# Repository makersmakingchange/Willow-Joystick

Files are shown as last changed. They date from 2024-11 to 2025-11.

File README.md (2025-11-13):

# Willow Joystick

## Overview
The Willow Joystick is a cost-effective, low force joystick that can be used for adaptive gaming or computer access. This joystick is intended for users with very low strength or range of motion. The joystick only requires about 25 grams of force to operate, and has a range of motion of ± 7.5° or about ±5 mm. 

The Willow Joystick has a variety of options for customizing it for the user:
 - Swappable Toppers: there are 7 different topper designs, including one that can be used with heat moldable polymer for a custom fit. 
 - Wrist Ramps: there are several wrist rest options for  supporting the user's arm.
 
The Willow is made up of the Willow Joystick and the Willow Hub. The Joystick is the primary user interface and contains a low-force Hall-Effect joystick. The Hub has a display that provides a graphical interface for independently adjusting settings, as well as it provides the connection to the host device and up to three external assistive switches with 3.5 mm jacks.

The Willow is compatible with a range of host devices that can support a USB Mouse, a USB Gamepad and/or a Bluetooth Mouse. Compatible devices include PC and Mac computers and laptops, Android, iOS, and Windows smartphone and tablets, and the Xbox Adaptive Controller. As a USB joystick, the Willow is not compatible with the Sony Playstation Access Controller.  

The joystick has adaptors for both ¼-20 mounting arms and RAM-B ball mount arms and has an optional nonslip base for use on a table. There is also a modifiable wrist ramp to help raise a user’s wrist while using the joystick.

The device is comprised of off-the-shelf electronics and hardware, a custom PCB and 3D printed parts. The overall cost of materials (including materials required in bulk) for a single build is about $180 (plus shipping). In larger quantities, the cost of materials is closer to $135.

The Willow Joystick is Open Assistive Technology (OpenAT) and is certified as Open Source Hardware by the Open Source Hardware Association under the OSHWA UID [CA000062](https://certification.oshwa.org/ca000062.html). Under the terms of the open source licenses, the device may be built, used, and improved upon by anyone.

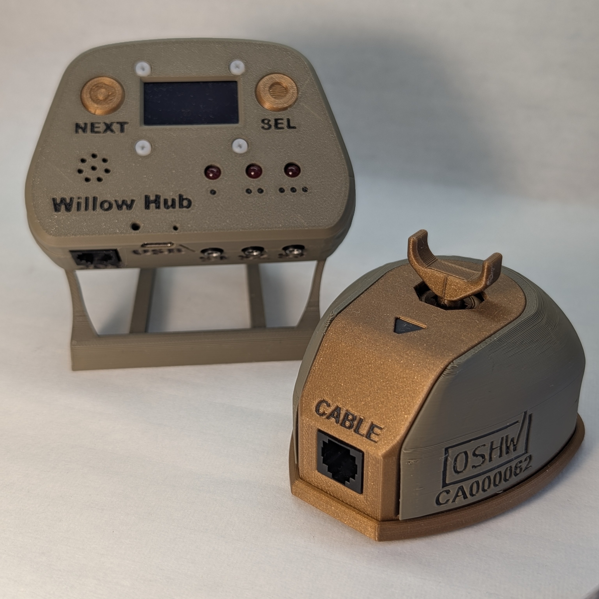
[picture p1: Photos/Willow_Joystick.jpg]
Willow joystick.
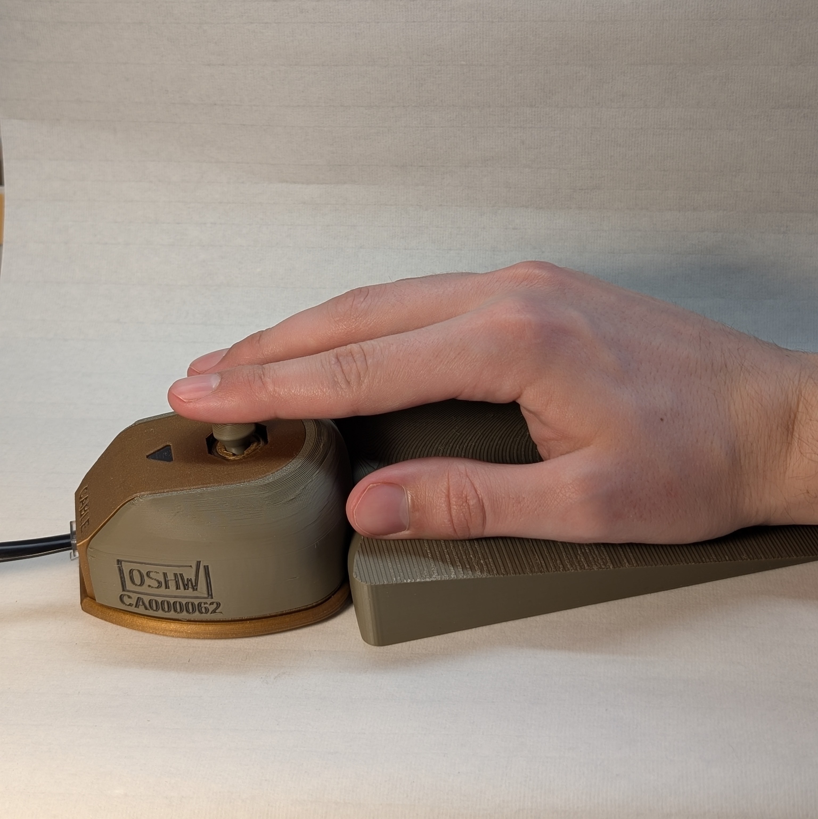
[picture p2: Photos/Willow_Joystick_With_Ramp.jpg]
Willow joystick.
 

## Makers Making Change Assistive Device Library
 - https://www.makersmakingchange.com/s/product/willow-joystick/01tJR000007iDn7YAE

## OpenAT Joysticks
This design is part of the [OpenAT Joystick Project](https://github.com/makersmakingchange/OpenAT-Joysticks), a collection of open source designs for digital access and adapted gaming.  

## How to Obtain the Device
### 1. Do-it-Yourself (DIY) or Do-it-Together (DIT)

This is an open-source assistive technology, so anyone is free to build it. All of the files and instructions required to build the device are contained within this repository. Refer to the Maker Guide below for detailed build instructions.

### 2. Request a build of this device

You may also submit a build request through the [Makers Making Change Assistive Device Library Listing](https://www.makersmakingchange.com/s/product/willow-joystick/01tJR000007iDn7YAE) to have a volunteer maker build the device. As the requestor, you are responsible for reimbursing the maker for the cost of materials and any shipping.

### 3. Build this device for someone else

If you have the skills and equipment to build this device, and would like to donate your time to create the device for someone who needs it, visit the [MMC Maker Wanted](https://makersmakingchange.com/maker-wanted/) section.

## Build Instructions

### 1. Read through the Maker Guide
The [Maker Guide](/Documentation/Willow_Joystick_Maker_Guide.pdf) contains all the necessary information to build this device, including tool lists, assembly instructions, programming instructions and testing.

### 2. Order the Off-The-Shelf Components
The [Bill of Materials](/Documentation/Willow_Joystick_BOM.xlsx) lists all of the parts and components required to build the device.

### 3. Print the 3D Printable components
All of the files and individual print files can be found in the [/Build_Files/3D_Printing_Files](/Build_Files/3D_Printing_Files/) folder. 

### 4. Assemble the Willow Joystick
Reference the Assembly Guide section of the [Maker Guide](/Documentation/Willow_Joystick_Maker_Guide.pdf) for the tools and steps required to build the device.

## How to improve this Device
As open source assistive technology, you are welcomed and encouraged to improve upon the design. 

## Files
### Documentation

| Document             | Version | Link |
|----------------------|---------|------|
| Design Rationale     | 1.0     | [Willow_Joystick_Design_Rationale](/Documentation/Willow_Joystick_Design_Rationale.pdf)     |
| Maker Guide          | 1.0.1     | [Willow_Joystick_Maker_Guide](/Documentation/Willow_Joystick_Maker_Guide.pdf)     |
| Bill of Materials    | 1.0     | [Willow_Joystick_Bill_of_Materials](/Documentation/Willow_Joystick_BOM.xlsx)     |
| User Guide           | 1.0     | [Willow_Joystick_User_Guide](/Documentation/Willow_Joystick_User_Guide.pdf)    |
| Changelog            | 1.0.1     | [Changelog](CHANGES.txt)     |

### Design Files
 - [CAD Files](/Design_Files/CAD_Design_Files)
 - [PCB Files](/Design_Files/PCB_Design_Files)

### Build Files
 - [3D Printing Files](/Build_Files/3D_Printing_Files)
 - [PCB Build Files](/Build_Files/PCB_Build_Files)
 - [Firmware Files](/Build/Firmware_Files)

## License
Copyright (c) 2025 Neil Squire Society.

This repository describes Open Hardware:
 - Everything needed or used to design, make, test, or prepare the Willow Joystick is licensed under the [CERN 2.0 Weakly Reciprocal license (CERN-OHL-W v2) or later](https://cern.ch/cern-ohl ) .
 - All software is under the [GNU General Public License v3.0 (GPL-3.0)](https://www.gnu.org/licenses/gpl.html).
 - Accompanying material such as instruction manuals, videos, and other copyrightable works that are useful but not necessary to design, make, test, or prepare the Willow Joystick are published under a [Creative Commons Attribution-ShareAlike 4.0 license (CC BY-SA 4.0)](https://creativecommons.org/licenses/by-sa/4.0/) .

You may redistribute and modify this documentation and make products using it under the terms of the [CERN-OHL-W v2](https://cern.ch/cern-ohl).
This documentation is distributed WITHOUT ANY EXPRESS OR IMPLIED WARRANTY, INCLUDING OF MERCHANTABILITY, SATISFACTORY QUALITY AND FITNESS FOR A PARTICULAR PURPOSE.
Please see the CERN-OHL-W v2 for applicable conditions.

Source Location: https://github.com/makersmakingchange/Willow-Joystick

## Attribution
The Willow Joystick was designed by Makers Making Change / Neil Squire Society.
The hardware and firmware for the Willow Hub is based on the [LipSync Hub]() designed by Makers Making Change / Neil Squire Society. 

<!--- This is the attribution for the template. --->
The documentation template was created by Makers Making Change / Neil Squire Society and is used under a CC BY-SA 4.0 license. It is available at the following link: [https://github.com/makersmakingchange/OpenAT-Template](https://github.com/makersmakingchange/OpenAT-Template)

The Willow incorporates several commercially available open source hardware components:
 - [Adafruit TLV493D Triple-Axis Magnetometer - STEMMA QT / Qwiic](https://www.adafruit.com/product/4366). The PCB design is available under a CC-BY-SA 4.0 license at https://github.com/adafruit/Adafruit-TLV493D-PCB. 
 - [Adafruit 128X64 monochrome OLED Display Board](https://www.adafruit.com/product/938). The PCB design is available under a CC-BY-SA 4.0 license at https://github.com/adafruit/Adafruit-128x64-Monochrome-OLED-PCB.
 - [SparkFun Qwiic Adapter Board (DEV-14495)](https://www.sparkfun.com/products/14495). The PCB design is available under a CC-BY-SA 4.0 license at https://github.com/sparkfun/Qwiic_Adapter.   
 - [SparkFun RJ11 Breakout Board (BOB-14021)](https://www.sparkfun.com/products/14021). The PCB design is available under a CC-BY-SA 4.0 license at https://github.com/sparkfun/RJ11_Breakout. 

The Willow firmware utilizes the Arduino development platform, an open-source electronics platform based on easy-to-use hardware and software. Arduino is developed and maintained by the Arduino community, and the project wouldn't be possible without their contributions.
Arduino is a registered trademark of Arduino AG. For more information about Arduino and to contribute to the community, visit the official Arduino website at www.arduino.cc.
The Willow Firmware code uses several libraries:
 - [Adafruit_BusIO](https://github.com/adafruit/Adafruit_BusIO)  by Adafruit
 - [Adafruit_GFX](https://github.com/adafruit/Adafruit-GFX-Library) by Adafruit
 - [Adafruit_Sensor](https://github.com/adafruit/Adafruit_Sensor) by Adafruit
 - [Adafruit_SSD1306](https://github.com/adafruit/Adafruit_SSD1306) by Adafruit
 - [ArduinoJson](https://github.com/bblanchon/ArduinoJson) by Benoit Blanchon
 - [TLV493D-A1B6](https://github.com/Infineon/TLV493D-A1B6-3DMagnetic-Sensor) by Infineon Technologies

### Contributors
<!--- List the names of the people that contributed to the design. This could include the original source of the idea, designers, testers, documenters, etc. --->
Designers:
 - Brad Wellington, Neil Squire Society / Makers Making Change.
 - Stephen Moyer, Neil Squire Society / Makers Making Change.
 - Josie Versloot, Neil Squire Society / Makers Making Change.
 - Tyler Fentie, Neil Squire Society / Makers Making Change.
 - Jake McIvor, Neil Squire Society / Makers Making Change.
 - Milad Hajihassan, Neil Squire Society / Makers Making Change.

<!--- Testers:
 - <TESTER 1>
 - <TESTER 2> --->

---
<!-- ABOUT MMC START -->
## About Makers Making Change
<!--- This is standard boilerplate for Makers Making Change. No changes should be required. --->
[Makers Making Change Logo](https://www.makersmakingchange.com/)

Makers Making Change is a program of [Neil Squire](https://www.neilsquire.ca/), a Canadian non-profit that uses technology, knowledge, and passion to empower people with disabilities.

Makers Making Change leverages the capacity of community based Makers, Disability Professionals and Volunteers to develop and deliver affordable Open Source Assistive Technologies.

 - Website: [www.MakersMakingChange.com](https://www.makersmakingchange.com/)
 - GitHub: [makersmakingchange](https://github.com/makersmakingchange)
 - Instagram: [@makersmakingchange](https://www.instagram.com/makersmakingchange)
 - Facebook: [makersmakechange](https://www.facebook.com/makersmakechange)
 - LinkedIn: [Neil Squire Society](https://www.linkedin.com/company/neil-squire-society/)
 - Thingiverse: [makersmakingchange](https://www.thingiverse.com/makersmakingchange/about)
 - Printables: [MakersMakingChange](https://www.printables.com/@MakersMakingChange)

### Contact Us
For technical questions, to get involved, or to share your experience we encourage you to [visit our website](https://www.makersmakingchange.com/) or [contact us](https://www.makersmakingchange.com/s/contact).
<!-- ABOUT MMC END -->

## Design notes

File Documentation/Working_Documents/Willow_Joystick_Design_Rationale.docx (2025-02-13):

# Overview

The Design Rationale is intended to provide designers and maker information about the design process and design decisions behind the development of the Willow Joystick, a low force magnetic joystick for users with low strength.

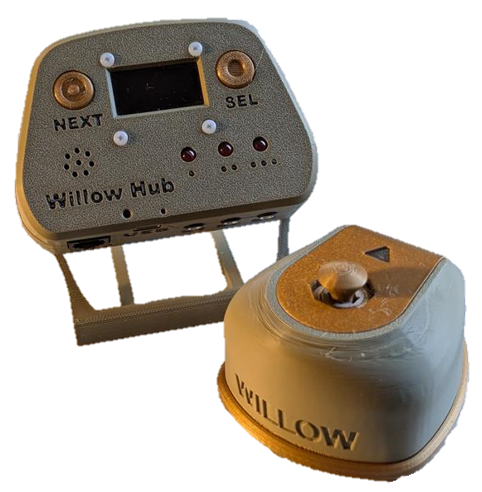
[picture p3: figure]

# Introduction

After developing the LipSync, an opportunity arose to take the magnetic gimbal system and develop it further to create a low force addition to the MMC joystick library.

The Willow is intended for users that find the existing joystick options in the MMC library too high force or require too large of a range of motion, and need a lower force, lower range of motion option.

The Willow would be useful for users with conditions that limit their strength and range of motion, such as Spinal Muscular Atrophy.

# Requirements

The goals and requirements outlined here are to assess if a device would meet the needs of a user, and determine when a design is sufficient for release.

## User Needs / Goals

G01 | Requires low force to operate
G02 | Compatibility with existing toppers
G03 | Device should be ergonomic and not put strain on the user’s wrist during use
G04 | Device should have a physical range of motion comparable to LipSync or typical gaming thumbstick (e.g., ±10 mm)
G05 | Minimize device envelope.

## Requirements

F01 | With the default topper, the joystick must require 30 g or less of force to fully displace the joystick
F02 | Linear range of the joystick must be between a minimum of ±5 mm and a maximum of ±20 mm.
F03 | The device is operable in two operating modes: Joystick HID and Mouse HID.
F04 | A secondary user must be able to switch between operating modes
F05 | A Primary User should be able to switch between operating modes
F06 | Device must give the user visual or auditory feedback on the current operating mode.
F07 | A secondary user must be able to perform a neutral calibration of the joystick
F08 | The primary user should be able to perform a neutral calibration of the joystick
F09 | Device should have swappable toppers.
F10 | Devices should have toppers that are swappable by a Secondary User.
F11 | Device should utilize the Oak modular topper interface.
F12 | Device must be mountable, either compatible with the OpenAT Joystick mounting adaptor or have a built in ¼”-20 UNC thread
F13 | Device must output USB HID directly OR be compatible with an existing interface (e.g., LipSync Hub, Forest Hub)
F14 | Design must be smooth with no sharp edges
F15 | When passively resting on a desk or flat surface, the device must not slide when a horizontally applied force equal to the operating force is applied to the joystick.
F16 | When passively resting on a flat surface, the device must not tip over when a horizontally applied force equal to the operating force is applied to the joystick in any direction.
F17 | Device produced a proportional output through the range of motion.
F18 | Device must provide two axes of output.
F19 | Device must have an input deadzone.
F20 | Device must be compatible with the XAC

## Evaluation Criteria

NF01 | If device is bumped, it should not send an input to the connected device
NF02 | Design must adhere to intuitive operations
NF03 | Hysteresis (how well the device returns to center)
NF04 | Device should have an input deadzone that is adjustable by a Secondary User.
NF05 | Device should have a sensitivity that is adjustable by a Secondary User.
NF06 | Device should have a way to invert the axes by a Secondary User.
NF07 | Device should be able to withstand a drop of 3 feet onto a hard surface
NF08 | Device should function when mounted vertically or upside down

## Constraints

C01 | Design must use off the shelf or 3D printed parts
C02 | Design must use 3D printed plastic for gimbal and enclosure
C03 | Device must not use batteries
C04 | Commercial components should be available from multiple sources
C05 | The parts should be sourced from as few suppliers as possible to lower shipping costs
C06 | Parts must be available in low quantities
C07 | Parts must not be region specific
C08 | Device must be safe for the user and disclaim any potential hazards such as magnets
C09 | Device should be assembled with commonly available tools as volunteer made OpenAT
C10 | Only use hardware found in the LipSync gimbal in the Willow gimbal
C11 | The number of fastener types in the device should be minimized
C12 | The Willow joystick must work on the same magnetic gimbal principal as the LipSync
C13 | Assembly should not require high strength or torque
C14 | Device should be shippable within a Canada Post flat rate shipping box.
C15 | Device should cost less than the BoM cost for the LipSync 4

# Stakeholders

- MMC
- GAME Checkpoints
- Neil Squire Solutions
- AbleGamers
- Primary users
- Secondary users
- Makers

## Description of Targeted User

The targeted user of the Willow Joystick is someone who has limited to full range of motion with their hands (or other body part used to control the joystick, such as the chin), but limited strength. This includes users with spinal muscular atrophy (SMA), arthritis, muscular dystrophy, and multiple sclerosis.

This includes users that would use a LipSync, but either do not want the sip and puff aspect, or do not want to control it with their mouths.

# Research

## Commercially Available Options

Options that can be purchased but not made by a maker.

### Celtic Magic Feather

Title / Name of device | Feather Joystick
Link | https://www.celticmagic.org/feather
Author | Celtic Magic
Cost | 600 GBP

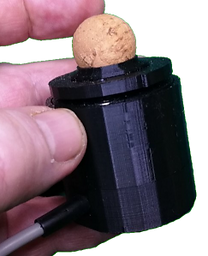
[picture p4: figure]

The Feather Joystick by Celtic Magic is a magnetic low force joystick and mouse with a sensitivity of 5 grams. The method of sensing/magnetic joystick mechanism is unknown. It comes in three different models, mouse, joystick, and game control mixer. It has an optional hand support system that allows the Feather and a variety of switches to be supported relative to a user’s hand. It also has a variety of optional addons, such as a light bar for user feedback that mounts to a PC monitor.

Requirements Met | Requirements Unmet
G01, G06, G07 F01, F02, F03, F04, F09, F10, F12, F13, F14, F17, F20, F21, F22, F23 NF02 C03, C05, C08, C14 | G02, G03, G04 F04, F05, F11 C01, C10, C12, C15

#### Useful Design Features

- Low usage force
- Adjustable force
- Swappable Toppers
- Adjustable configuration through app
- Works with adaptors and stands
- Button inputs

### Mo-Vis Micro Joystick

Title / Name of device | Micro Joystick
Link | https://www.mo-vis.com/products/wheelchair-joysticks/micro-joystick
Author | Mo-Vis
Cost | $3400 CAD

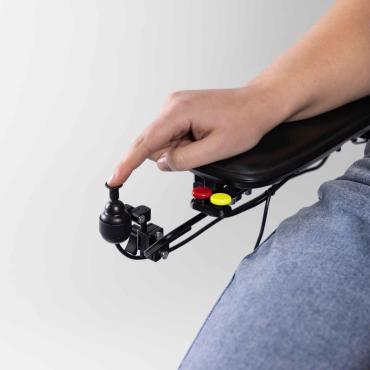
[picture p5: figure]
Micro Joystick finger with Micro Joystick Cup (15.5 mm)

The Micro Joystick is a joystick module that can be connected to a wheelchair to control the wheelchair functions. It is designed for users with reduced range of motion and muscle strength. The same mechanism is also used in the Mo-Vis HID Joystick.

Requirements Met | Requirements Unmet
G01, G05, G06, G07 F01, F02, F13, F14, F17, F18, F20 NF02 C03 | G02, G03, G04 F09, F10, F11 C01, C02, C04, C05, C06, C10, C12

#### Useful Design Features

- Low force
- Small size
- Swapable toppers
- LED for user feedback

## DIY / Maker-Friendly Options

Options that can be made by a maker.

### Celtic Magic Dangle Joystick

Title | Dangle Joystick
Link | https://www.celticmagic.org/dangle
Author | Celtic Magic
License | OSHW Definition 1.0
Cost | 55 GBP
Test Build (Y/N) | No
Add to Library (Y/N) | No

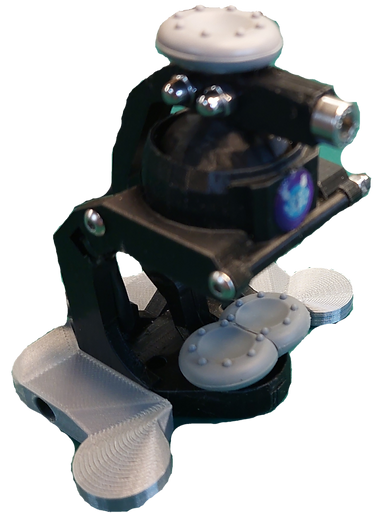
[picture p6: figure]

The Dangle Joystick is a low force, inverted, magnetically centered joystick with an operating force of 10 grams. You can build your own Dangle for 55 pounds, or buy one prebuild for 190 pounds.

Requirements Met | Requirements Unmet
G01, G02, G03, G05, G06 F01, F02, F13, F14, F15, F20, F21, F22 NF02 C01, C02, C03, C04, C05, C06, C08, C09, C15 | G04, G07 F03, F04, F05, F09, F10, F11 C10, C12

#### Useful Design Features

- Low force operation
- Integrated button
- Configuration adjustable via app
- Optional camera mount

<INCLUDE ANY DESIGN FEATURES OF THE DEVICE THAT COULD / SHOULD BE CONSIDERED IN THE DESIGN OF ANOTHER DEVICE>

## Joystick Force and Range of Motion Comparison

Joystick | Operational Force | Range of Motion
Celtic Magic Feather | 5, 10, 15, 20 g | Up to +/- 6 Degrees
Celtic Magic J1, J2, J3 | 60 or 20 g | Unknown
Celtic Magic Dangle Joystick | 10 g | +/-35 degrees
Mo-Vis Micro Joystick | 8 or 5 g | 3 mm movement
LINX 400 Compact Remote | 81 g | Unknown
ASL Micro Extremity Control | 18 g | Unknown
LipSync | 50 g | +/-10 degrees | 10 mm
Oak Joystick | 525 g | +/- 25 degrees
Spruce Joystick | 75 g | +/-30 degrees
Birch Joystick | 115 g | +/- 2mm | +/- 2 mm
Xbox One controller | 57-86 g | +/- 23 degrees

## Research Summary

Existing low force joysticks are in the 20g or less range, with a wide range of angles. Most of the extreme low force joysticks are in the ~+/-6 degrees range, while the rest of the joysticks do not go past +/-35 degrees.

# Ideation

## Key Features

### Output Architecture: Microcontroller vs Hub

#### Weighted Decision Table

##### Options

Standalone Device

The first option for the Willow joystick is a standalone, self-contained device. This version of the willow would have the microcontroller, magnetic gimbal, any user feedback or user inputs all within the same enclosure. This device would have between two and zero user inputs, with user feedback limited to a small number of LEDs or NeoPixels and potentially a buzzer.

LipSync Hub

The LipSync hub option involves using the LipSync hub as the brains, switch input, and feedback of the Willow joystick. The joystick unit itself would just contain the magnetic gimbal, and the joystick unit would connect to the hub via RJ11 cable, just like the LipSync joystick. This would require reprogramming of the LipSync hub to distinguish the Willow and the Joystick, as well as the addition of a Willow mode that works without the sip and puff mechanism.

Forest Hub

The Forest Hub option involves using the Forest Hub as the brains, switch input, and feedback of the Willow joystick. The joystick unit itself would just contain the magnetic gimbal, and the joystick unit would connect to the Hub via RJ11 cable. This would require the Forest Hub to be updated to recognize the Willow, as well as the ability to translate the magnetic field readings into joystick output, similar to the joystick on the analog out.

Custom Hub

The Custom Hub option involves creating an entirely new hub for use with the willow joystick. This hub would be used as the brains, switch input and user feedback of the willow joystick. The hub would need to be created from scratch, with all that that entails. This would add another project on par with the forest hub to the Willow project.

##### Criteria

CAD Design Effort

CAD Design Effort is the amount of engineering time required to perform the CAD design on the 3D printed parts

PCB Design Effort

PCB Design Effort is the amount of engineering time required to perform the PCB design

Ease of Assembly

Ease of assembly is a maker targeted metric. It measures the ease of assembling the complete Willow setup.

MMC Supplier Role

Measures how many stocked parts common to MMC devices that the Willow uses.

Modular Toppers

Measure of if the device has modular toppers

Ease of Independent Customizability

Customizability is a measure of how customizable the device is. This includes swappable toppers, adjustable sensitivity, calibrations, and other settings users can tweak to improve how the device works for them.

Integrated Second Joystick

Measures if the devices has an integrated second joystick.

Upkeep Effort

Upkeep effort is a measure of how much work Makers Making Change must do to keep the device in a working and functional state. A one and done device would be rated high, where something that works with multiple devices and as such would need to be tested and ensure compatibility with all rated devices every update would be rated lower.

Programming Effort

Programming Effort is the amount of engineering time required to create or adapt code to make the device functional.

Size

Size refers to the overall size of the setup, including the joystick unit itself, as well as any hubs or switches.

Setup

Setup is a measure of how complicated the setup of each device is. This is an aggregate of the number of components involved (joystick, hub, switches) that must be positioned and mounted, as well as the amount of restrictions on how the components must be mounted, i.e. if text on a display needs to be legible vs an LED lighting up.

User Training

User Training is a measure of how intuitive it is to use the device, and how much training is required to get the user up and running with the device.

Cost

Cost refers to the overall cost of the device setup, including any hub, PCBs, etc. A rating of 1 is an equivalent price to the LipSync, with each point worth ~$15-$20

Interactability

Interactability is a measure of how many different ways the user can interact with the device. This includes the joystick but is also a measure of how many switch inputs the device has.

Feedback

Feedback is a measure how much feedback the user gets from the device.

##### Weighted Decision Matrix – Device Architecture

Options | Weights | Standalone | LipSync Hub | Forest Hub | Custom Hub
CAD Design Effort | 2 | 4 | 6 | 6 | 1
PCB Design Effort | 1 | 5 | 10 | 10 | 3
Programming Effort | 3 | 5 | 1 | 4 | 3
Ease of Assembly | 2 | 7 | 6 | 4 | 6
MMC Supplier Role | 1 | 6 | 8 | 7 | 4
Upkeep Effort | 1 | 8 | 4 | 5 | 7
Cost | 5 | 7 | 3 | 4 | 4
Size | 5 | 8 | 5 | 6 | 6
Setup | 2 | 7 | 3 | 4 | 4
User Training | 4 | 7 | 6 | 5 | 5
Modular Toppers | 2 | 5 | 5 | 5 | 5
Ease of Independent Customizability | 4 | 3 | 9 | 6 | 7
Interactability | 1 | 4 | 8 | 7 | 7
User Feedback | 4 | 3 | 8 | 6 | 6
Integrated Second Joystick | 1 | 0 | 0 | 6 | 6
Analog Output | 3 | 7 | 0 | 10 | 8
Total | | 232 | 200 | 233 | 214

The weights in this decision matrix were based on input from two designers.

#### Microcontroller Options

Criteria for microcontrollers:

Requirements

- Connect to the magnetic sensor via Stemma cable
- Provide user visual feedback
- Ability for user to interact with the microcontroller to change modes

Bonuses

- Minimize cost
- Minimize footprint
- Bluetooth
- Analog output for TRRS

Microcontroller | Cost | Footprint (mmxmm) | Stemma | Bluetooth | Analog Out | Other | Link
SAMD21 QT PY | $7.50 USD | 22x18 | Yes | No | Yes | | Link (https://www.adafruit.com/product/4600)
RP2040 QT PY | $9.95 USD | 22x18 | Yes | No | Yes | Dual core microcontroller | Link (https://www.adafruit.com/product/4900)
CH552 QT PY | $4.95 USD | 22x18 | Yes | No | Yes | Almost no Arduino support, compiles in C not C++ so most libraries don’t work | Link (https://www.adafruit.com/product/5960)
Seeed XIAO nrf52 | $9.90 USD | 22x18 | No | Yes | Yes | | Link (https://www.seeedstudio.com/Seeed-XIAO-BLE-nRF52840-p-5201.html)
CH32V203 QT PY | $4.95 USD | 22x18 | Yes | No | Unknown | Almost no Arduino support | Link (https://www.adafruit.com/product/5996)
nRF52840 ItsyBitsy | $19.95 USD | 36x18mm | No | Yes | Yes | | Link (https://www.adafruit.com/product/4481)
nRF52840 glasses driver | $24.95 USD | 58x19 | Yes | Yes | No | Has lots of unneeded sensors | Link (https://www.adafruit.com/product/5217)
Metro Mini 328 V2 | $14.95 USD | 44x18 | Yes | No | Yes | | Link (https://www.adafruit.com/product/2590)
ESP32 Pico QT Py | $14.95 USD | 22x18 | Yes | Yes | Yes | Also has Wi-Fi | Link (https://www.adafruit.com/product/5395)

Microcontroller recommendation

If Bluetooth is not a requirement, the SAMD21 QT PY is the best choice for its low cost, small footprint, stemma and analog capabilities while not having any unneeded features such as extra sensors.

If Bluetooth is a requirement, the ESP32 Pico QT PY is the best choice for its small footprint, Bluetooth capabilities, analog output, stemma port while minimizing unnecessary features.

Microcontroller Pros

- Able to function as a standalone device
- Low cost

Microcontroller Cons

- To add capabilities beyond what is included with the microcontroller (More sensors or button inputs) either a stemma module or a protoboard and wires are required.
- Limited feedback abilities

#### Hub Options

Hub | Price | Inputs | Feedback | Adjustability | Output Modes
LipSync Hub | $107.48 | - 3x 3.5mm switch Jacks - RJ11 i2c connector - 2x onboard push buttons | - Audio buzzer - 3x LEDs - Text display | - Neutral reset - Extent calibration - Cursor speed adjustment | - HID Gamepad - HID Mouse - Bluetooth - USB
Forest Hub | $78.54 | - 5x 3.5mm switch Jacks - RJ11 i2c connector - 2x onboard push buttons - 3.5mm TRRS jack | - Audio buzzer - 5x RGB LEDs | - Neutral reset - Cursor speed adjustment | - HID Gamepad - HID Mouse - USB

To make the willow joystick work with the hubs, the hubs themselves would need a firmware update. The hubs would need the basic programming added to allow them to translate the readings from the magnetic sensor into the HID output. They would also need to have an addition that allows them to recognize when a willow joystick is connected. The forest hub would just need to check if the magnetic sensor is attached, but the LipSync hub would need to be able to tell the difference between a willow joystick and a LipSync joystick. The LipSync hub already has the firmware required to convert magnetic sensor readings into HID, although if the order of magnet and sensor is reversed a slightly different version would have to be used for the Willow.

After reviewing the firmware of both the Forest hub and the LipSync hub, the firmware of the LipSync is much more complicated than the firmware of the Forest, with the functions spread across 16 different files. To make the Willow compatible with the LipSync Hub, a member of the LipSync development team who is familiar with the code would be required to help with the coding process to keep the project on schedule.

Hub Pros

- Increased user feedback
- Integrated switch inputs
- Integrated neutral or extent calibration
  - Extent calibration more difficult with forest, text makes it easier
- Integrated cursor speed adjustment

Hub Cons

- Increased cost
- Joystick cannot be used as a standalone
- Chosen hub will need a software update to include the software needed for the Willow
- No possibility of TRRS output

When deciding on the output architecture, the deciding factor between standalone and hub architecture depends on the expected use case. If the Willow is intended to be used like the Birch, as just a joystick with switch access being provided by another device such as the XAC or the Rocket Switch interface, then the standalone microcontroller option provides enough functionality for the intended use case. However, if the Willow is intended to have integrated switches, extensive user feedback, and extent calibration, it makes more sense to make it a hub output device to save development time and money.

### Neutral Calibration Options

- Microcontroller reboot/calibration on startup
- Externally triggered calibration

The two primary methods of neutral calibration are performing a calibration on microcontroller startup, and calibrating while the microcontroller is already powered on.

Calibration of the joystick during operation can be done by rebooting the microcontroller and taking advantage of the startup calibration. Most microcontrollers include a reboot button on the board itself, and the enclosure can be designed to allow a primary or secondary user to press the button to reboot the microcontroller and calibrate the neutral position.

Triggering the neutral calibration without rebooting the joystick would require an input to the microcontroller such as a button or switch jack or a movement pattern on the joystick such as holding it in a certain corner for a length of time then moving to another. If the microcontroller does not have an onboard button that is not connected to the reset pin, then an external button or jack would be needed to allow the user to trigger the reset. This button can either be directly wired to the microcontroller pins, or it can be connected a stemma button breakout board. This requires more parts, but works with accessible switches and preserves information between calibrations. A movement base calibration works without requiring additional hardware, but could be accidentally triggered by a user in the course of normal operation.

### Extent Calibration Options

Out of all the joysticks and hubs available through Makers Making Change, only the LipSync has extent calibration. The birch mentions deadzone calibration via serial in the ReadMe, but this is absent from the User Guide and Maker Guide. Extents calibration reads the value at each corner of the joystick range, and uses that information to properly calibrate the output along the full range of joystick motion.

When discussing extent calibration with a GAME checkpoint leader, we were told that while extent calibration could be a useful tool for Occupational Therapists or other trained secondary users, it could prove detrimental if the primary user or an untrained user attempted to perform an extent calibration and incorrectly calibrated it.

When performing an extent calibration on the LipSync, the user follows the directions on the screen, holding the mouthpiece in the four corners until the LipSync beeps.

To perform this type of extent calibration, the LipSync needs an input to initiate the calibration, and feedback to inform the user when to move to each corner. The text display also allows the instructions to be displayed to the user in real time, instead of having to refer to a user guide. This is not necessary for an extents calibration, but it does greatly simplify the process.

If using a hub, the extent calibration requirements are largely already met. The hubs have enough inputs that the user can use one to initiate an extents calibration, and both hubs have user feedback to time the different steps of the process. The LipSync Hub also has the text based display to show the steps in real time. The forest currently has no build in extent calibration, so that would need to be added via the same software update that adds Willow compatibility.

When using a microcontroller, the user feedback and input need to be provided. The options for providing input are the same as the options for a non reboot neutral calibration. If the microcontroller does not have an onboard input button, and external button or switch jack would be required. These can either be soldered directly to the microcontroller pads or connected via the stemma port. To provide user feedback, most microcontrollers from Adafruit have an LED, and some come with a NeoPixel LED that can be used to give feedback in any colour. Additional audio or visual feedback can be added by wiring to the microcontroller pins or added via stemma port.

### Analog Output

#### HID Remapper

https://github.com/jfedor2/hid-remapper

The HID Remapper is a configurable device that allows the remapping of inputs from HID devices. There are currently 9 different form factors of the device, 8 custom boards and a prebuild microcontroller from Adafruit. The v7 board is designed for use with the XAC and the Sony Access Controller (SAC), and has four analog outputs that work with the XAC. The four analog outputs are intended to be used as two analog joysticks, and two analog trigger inputs.

The device is programmed and powered through the USB C port, the USB A ports on the top are for HID input, and the 3.5mm jacks are for outputs. In addition to the 4 analog outputs, there are also 10 3.5mm switch outputs.

This is currently the only version of the HID remapper that supports analog outputs.

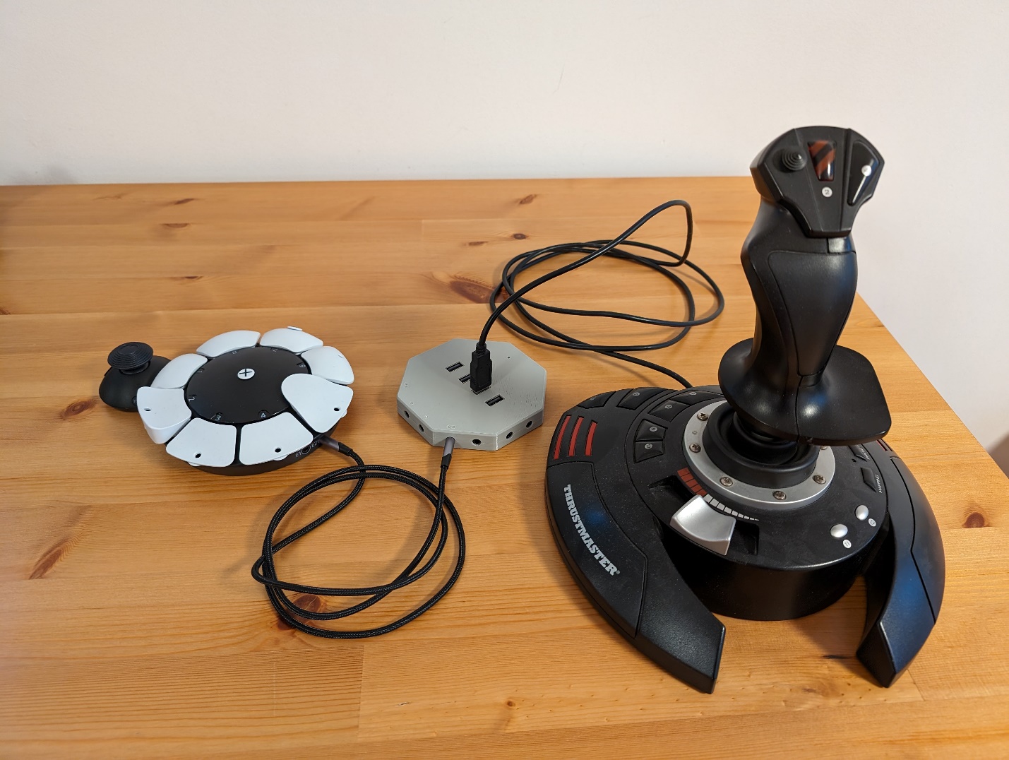
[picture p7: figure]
Connecting a USB joystick to the PlayStation Access controller using HID Remapper custom board v7

Figure 1: HID Remapper V7

#### Integrated Analog Output

An option for analogue outputs is to integrate them into the device itself. Including a 3.5mm TRRS jack in the device or associated hub allows two of the PWM ports of the microcontroller to be used to emulate the output of the potentiometers in an analog joystick. The voltage from the connected controller can be measured by an analog input pin to determine the expected output voltages for the different joystick positions.

### Centering Strength Adjustment

There are two general methods available to change the centering force of the Willow gimbal

- Change the distance between the gimbal and sled magnet
- Change the strength of the sled magnet

For the sake of keeping the strength adjustment user friendly, making changes to the magnet in the gimbal itself will be disregarded, focusing on making changes to the magnet in the sled which is more accessible to the user.

Changing the distance between the sled and gimbal allows for the strength to be changed without changing the magnet used. This can be done by using a screw to advance or retract the magnet, as well as having a variety of locations in the sled that the magnet can be mounted in. Mounting the magnet in different locations in the sled would require the sled to be opened and the magnet moved. Changing the position of the magnet using a screw allows for a secondary user to change the strength without opening the enclosure while allowing the strength to be adjusted anywhere between the two extremes.

Changing the strength of the sled magnet can be done in two ways. The first way that it can be done is changing the magnet used in the sled for a different magnet with a stronger field. The second method is to add more magnets. This does have diminishing returns as the number of magnets increases. The following is an excerpt from the LipSync Design rationale when exploring this option for the LipSync Gimbal

“When stacking magnets, the magnetic force increases until the thickness of the stack reaches the diameter of the magnets [first4magnets.com (https://www.first4magnets.com/tech-centre-i61/frequently-asked-questions-i69)]. Since the magnets used in the LipSync are 2.5mm x 8mm, 3 to 4 can be stacked before reaching diminishing returns. This is demonstrated in a graph showing the force vs thickness of the magnet. Note the X axis does not increase linearly. [totalelement.com (https://totalelement.com/en-ca/blogs/working-with-neodymium-magnets/will-stacking-magnets-together-make-them-stronger)]

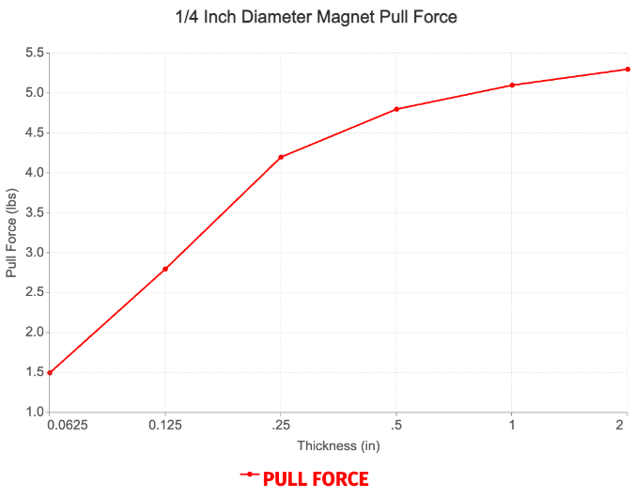
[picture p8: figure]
Magnet Pull Force Chart

Figure 2. Magnetic Force with Greater Thickness.

“

#### Pros and Cons of Different Mounting Methods

Method | Pros | Cons
Different mounting locations | - Only uses one magnet | - Requires disassembling and reassembling the sled - The need to support the magnet makes the number of possible places very small
Variable mounting location (screw) | - Adjustable over the entire range with no defined stops - Only requires one magnet | - The rotation of the screw changes the location of the magnet slightly, requiring a recalibration
Stronger magnet | - Only uses one magnet | - Requires all the magnets of different strengths have the same dimensions - Need to take apart the sled to change magnets
Using more magnets | - If the first magnet is secured, more can be stacked in behind it from the exterior of the enclosure to change strength without opening the enclosure | - Different steps of strength with no in-between - Diminishing returns with more magnets, up to 3 or 4

### Features of the LipSync Gimbal

The following is a list of all components of the LipSync gimbal, and a judgement of if they are required in the Willow joystick

#### Sled

- Centering magnet
  - Needed
- Sensing magnet
  - Needed, but could be moved to the gimbal
- Bearing seats
  - Needed
- Cable management
  - Needed
- Angle hard stops
  - Needed
- Sliding rails
  - Needed
- Arm tabs
  - Needed

#### Outer Gimbal

- Angle hard stops
  - Needed
- Cable management
  - Needed if the sensor stays on inner gimbal
- Part identifiers
  - Needed
- Bearing seats
  - Needed
- Bearing posts
  - Needed

#### Inner Gimbal

- Shield
  - Needed
- Luer adaptor
  - Unneeded
- Air path
  - Unneeded
- Pressure sensor
  - Unneeded
- Magnetic sensor
  - Needed, but could be moved to sled
- Centering magnet
  - Needed
- Angle hard stops
  - Needed
- Part identifiers
  - Needed
- Bolt holes
  - Needed, but only if magnetic sensor stays on inner gimbal
- Cable management
  - Needed, but only if magnetic sensor stays on inner gimbal
- Bearing posts
  - Needed

#### Bare Minimum Changes

- Remove pressure sensor, air tube, and Luer lock
- Design topper base that fits in Luer compartment

#### Maximum Changes

- Move magnetic sensor to the sled
- Remove pressure sensor, air tube and Luer Lock
- Move sensor magnet to inner gimbal
- Shrink the gimbal to remove the space
- Redesign Luer lock compartment to allow swappable toppers

### Topper Compatibilities

#### Oak

The Oak toppers all come in small, medium and large, and connect to the oak joystick via a collet system that clamps onto the stick of the oak joystick module. The toppers then screw onto the collet. The oak comes with 5 styles of topper.

- Ball
- Concave
- Convex
- Goalpost
- Stick

For this style of topper to work, it needs the joystick to have a stick that is identical to the stick found on the Oak joystick. A test would also have to be conducted to evaluate if the difference in hardness/friction between 3D printed plastic and the molded plastic of the Oak joystick affects the secureness of the collet connection. If the stick on the willow is 3D printed, it may be possible to print it directly with the thread used on the collet and bypass those parts entirely.

Pros

- Extremely secure connection
- Large variety of compatible toppers

Cons

- Collet is difficult to print and fragile, with layer lines
- Many parts required to attach the topper to the joystick
- Several toppers may be too heavy for use with a low force mechanism

Mass of Oak Toppers

Style | Small | Medium | Large
Ball | 11g | 18g | 29g
Concave | 10g | 15g | 14g
Convex | 4g | 9g | 10g
Goalpost | 14g | 17g | 19g
Stick | 34g | 50g | 67g

#### Birch

The Birch toppers connect to the joystick by a friction press fit on the joystick module. They are designed for the sliding motion of the Birch joystick, and not the rotating motion of a traditional joystick. The birch comes with 5 different styles of topper.

- Concave
- Large Dome
- Medium Dome
- Ring
- Small Dome

To make these work with the willow gimbal, the profile of the willow gimbal stick needs to match that of the Birch joystick.

Pros

- Simple design
- Minimal parts required to make the topper fit to the joystick

Cons

- Individual tolerances between printers can make press fit difficult
- Press fit may not work on the 3d printed plastic version of the Birch topper

Mass of Birch Toppers

Topper | Mass (g)
Concave | 1.0
Large Dome | 4.9
Medium Dome | 1.7
Ring | 1.5
Small Dome | 0.6

#### Evaluation Criteria

The primary criteria that toppers will be evaluated on are attachment and weight. Attachment is a measure of how well the topper attaches to the joystick stick. Weight is a measure of how much each topper weighs.

Since both sets of toppers were originally designed for different joysticks, it is entirely possible that both are unfit for the use case of the Willow.

The oak toppers have a large variety in their weights, ranging from 4 to 67 grams. This number does not include the weight of the collet and the topper nut, which weight 1.04 and 4.64 grams respectively. The current requirement for the centering force of the Willow is 30 grams or less. Since the weight of the topper is not applied perpendicular to the stick and the effective moment arm is the length of the topper multiplied by the sine of the angular displacement, it is possible to have a heavier topper than the max displacement force of the joystick. However, the heavier the topper, the lower the effective centering force, with the force getting lower the more it is displaced. If a compatible willow topper can be designed, either with a matching stick to the oak or with the correct thread that matches the topper nut, then the toppers with a mass of 15 grams or less could be trialed with the willow.

The Birch toppers are all below 5 grams in weight, with one being below 1 gram. They are designed for the Birch, which has a sliding motion, not a pivoting motion. The press fit has been known to have a tendency to pop off of the topper, especially the ring topper. While the Birch toppers are low weight enough to work with the willow, the lack of a secure attachment point makes them unsuitable for use with the willow.

### Features Vs Costs

Feature | Cost | Benefits
Magnetic Gimbal | $25.71 | Joystick core
Switch Inputs | $2.29/Switch Input | Allows the user switch inputs
LED Outputs | $0.42/LED | Single colour on/off visual feedback
NeoPixel Outputs | $1.47/NeoPixel, sold in 5 pack | Multicolour on/off visual feedback
Text Display | $30.47 | Text visual feedback
Audio Feeback | $0.92 | Musical note audio feedback
Tactile Buttons | $1.02/Button | Built in device button inputs
Bluetooth | ~$5 | Connect to devices without needing to plug into them

### Options for Multiple Joysticks

#### Analog Input

A simple way of having multiple joystick inputs is to have analog TRRS joystick inputs, such as on the forest hub. This allows for analog joysticks such as the oak or spruce to be used alongside the Willow. However, the downside to this is the fact that the analog joysticks in the MMC library are all higher force than the Willow, which was developed to provide a low force alternative. Using analog joysticks in addition to the willow would be difficult for someone who requires the low force of the willow to be able to use a joystick.

#### Multiple i2c buses

Since the same magnetic sensor is used in the gimbal of every Willow Joystick, there is no way to differentiate them when they are on the same i2c bus. Using a multiplexer would allow for multiple of the same sensors to be connected at the same time. However, the library used for the magnetic sensor does not have a method of verifying when a connection has been made, so verifying the number of joysticks attached to the central hub will be difficult and may rely on user input.

#### Multiple Complete Willows

The simplest option for using multiple joysticks is to simply use multiple independent joysticks instead of having a single central hub with multiple joysticks. This increases the overall cost of the setup significantly, but eliminates the design and usage challenges posed by the other methods.

## Ideation Decisions

Idea | Decision (Abandon, Modify, Proceed) | Justification
Standalone Architecture | Abandon | Hub option chosen
Hub Architecture | Proceed | - Allows for reuse of LipSync code - Provides large amount of user feedback - Existing neutral and extent calibration - Makes the willow compatible with future hub reworks - Adds switch inputs - Allows the joystick unit to be as simple as possible

# Conceptual Design

## Gimbal Design

### Concept 1: Existing LipSync Gimbal

A joystick made from an unchanged LipSync gimbal.

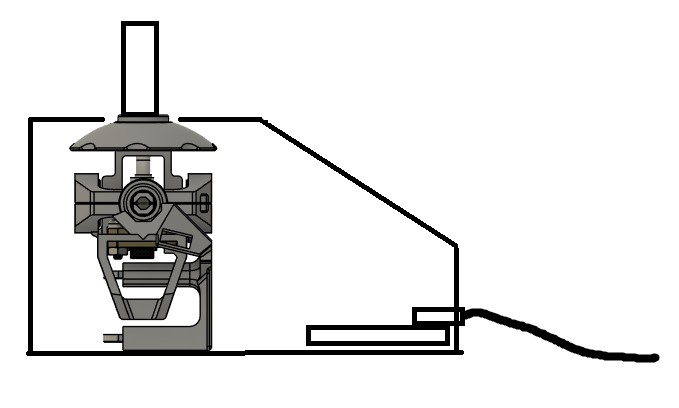
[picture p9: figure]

#### Physical Component / Enclosure

The gimbal used will be identical to the LipSync gimbal, but with the air path components not installed.

#### Electrical Components

In this version, both of the pressure sensors are removed, and the magnetic sensor is connected directly to the to the RJ11 jack.

#### Code Structure / Function

The software used is a version of the LipSync code that has been modified to have all pressure and sip/puff functions removed.

### Concept 2: Redesigned Magnetic Gimbal

A gimbal based on the principals used in the LipSync gimbal, but redesigned to make it as short and compact as possible.

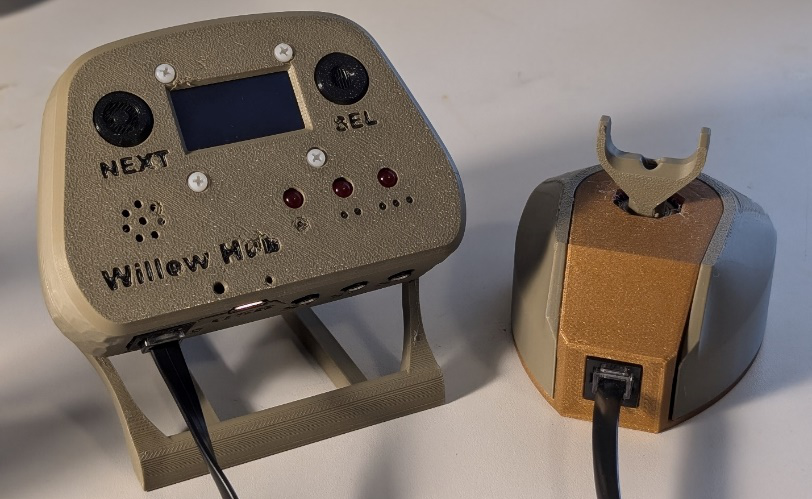
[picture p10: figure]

#### Physical Component / Enclosure

##### Willow Hub

The Willow Hub is a LipSync Hub that has been modified to replace the LipSync name with the Willow label.

##### Willow Joystick

The Willow joystick consists of two main components, the enclosure and the gimbal. The enclosure has a main base, which the gimbal sandwiches between, with the shell going overtop and securing everything in place. The gimbal is based off the LipSync gimbal, but compressed as much as possible to keep the profile of the Joystick low.

#### Electrical Components

##### Willow Hub

The Willow hub is electrically identical to the LipSync Hub.

##### Willow Joystick

The magnetic sensor is removed from the gimbal, and is instead mounted to the sled. This allows the extensive cable routing to be removed and the wiring simplified. The stemma cable from the magnetic sensor is directly connected to the RJ11 jack that is pinned in place in the enclosure.

#### Code Structure / Function

The software used is a version of the LipSync code that has been modified to have all pressure and sip/puff functions removed. Other minor changes have also been made, with one of the axis inverted and the deadzone expanded to account for the new sensor location and lower centering force.

## Concept Decisions

Concept | Decision (Abandon, Modify, Proceed) | Justification
Existing LipSync Gimbal | Abandon | - High profile - Significant portions of the gimbal were designed around the airpath which is no longer needed
Redesigned Magnetic Gimbal | Proceed | - Lower profile makes it more comfortable to use - All the initial CAD had been already done as a personal project working on a standalone Bonsai Joystick

Concept | Decision (Abandon, Modify, Proceed) | Justification
Existing LipSync Gimbal | Abandon | - High profile - Significant portions of the gimbal were designed around the airpath which is no longer needed
Redesigned Magnetic Gimbal | Proceed | - Lower profile makes it more comfortable to use - All the initial CAD had been already done as a personal project working on a standalone Bonsai Joystick

# Prototyping

## Prototype 1: Redesigned Magnetic Gimbal

A gimbal based on the principals used in the LipSync gimbal, but redesigned to make it as short and compact as possible.

### Physical Component / Enclosure

#### Willow Hub

The Willow Hub is a LipSync Hub that has been modified to replace the LipSync name with the Willow label.

https://github.com/makersmakingchange/LipSync/blob/main/Documentation/LipSync_BOM.csv

#### Willow Joystick

The Willow joystick consists of two main components, the enclosure and the gimbal. The enclosure has a main base, which the gimbal sandwiches between, with the shell going overtop and securing everything in place. The gimbal is based off the LipSync gimbal, but compressed as much as possible to keep the profile of the Joystick low.

Commercial Parts

Part | Image | Qty | Description | Link | Price (CAD)

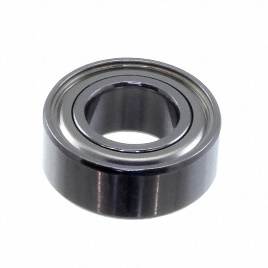
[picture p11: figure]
DDRI814ZZRA3P25LY121

Bearing | | 4 | Bearings for gimbal | Digikey (https://www.digikey.ca/en/products/detail/mechatronics-bearing-group/DDRI814ZZRA3P25LY121/9608362) | 4.44
Magnet | | 3 | Magnets for centering and sensing | Digikey (https://www.digikey.ca/en/products/detail/radial-magnets-inc/9029/5218824) | 1.07
M2.5 bolt | | 5 | Bolts to hold magnetic sensor and swappable topper | Digikey (https://www.digikey.ca/en/products/detail/essentra-components/50M025045P008/11638585) | 0.20
M2.5 nut | | 5 | Nuts to hold magnetic sensor and swappable topper | Digikey (https://www.digikey.ca/en/products/detail/essentra-components/04M025045HN/9677099) | 0.20
M3 nut | | 2 | Bolts to add threads for mounting adaptor | Digikey (https://www.digikey.ca/en/products/detail/keystone-electronics/4708/4499301) | 0.25

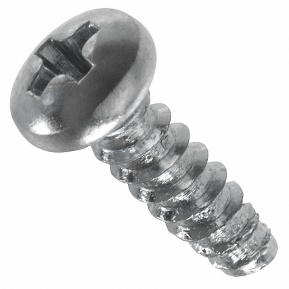
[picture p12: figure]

#4 screw | | 3 | Screws to hold enclosure together | Digikey (https://www.digikey.ca/en/products/detail/serpac/6005/307599) | 0.59

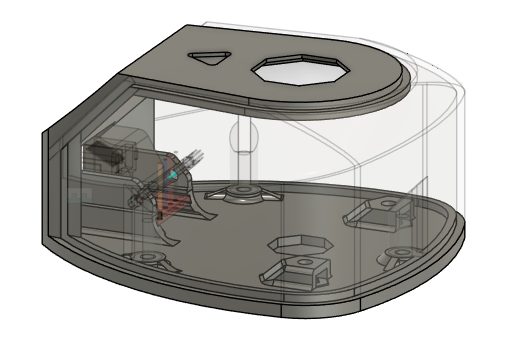
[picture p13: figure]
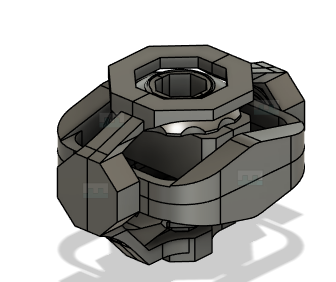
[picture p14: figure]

### Electrical Components

#### Willow Hub

The Willow hub is electrically identical to the LipSync Hub.

https://github.com/makersmakingchange/LipSync/blob/main/Documentation/LipSync_BOM.csv

#### Willow Joystick

The magnetic sensor is removed from the gimbal, and is instead mounted to the sled. This allows the extensive cable routing to be removed and the wiring simplified. The stemma cable from the magnetic sensor is directly connected to the RJ11 jack that is pinned in place in the enclosure.

Commercial Parts

Part | Image | Qty | Description | Link | Price (CAD)
Magnetic Sensor | | 1 | Sensor to read magnet angle | Digikey (https://www.digikey.ca/en/products/detail/adafruit-industries-llc/4366/10481837) | 8.64
Stemma Cable | | 1 | Connects the magnet sensor to the jack | Digikey (https://www.digikey.ca/en/products/detail/adafruit-industries-llc/4209/10230003) | 1.38

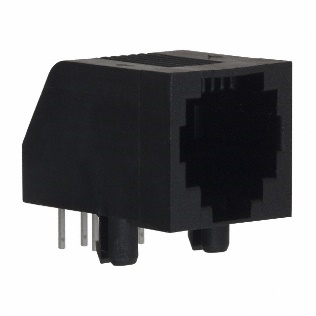
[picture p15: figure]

RJ11 jack | | 1 | Jack to connect the RJ11 cable | Digikey (https://www.digikey.ca/en/products/detail/te-connectivity-amp-connectors/5555165-1/769566) | 1.67

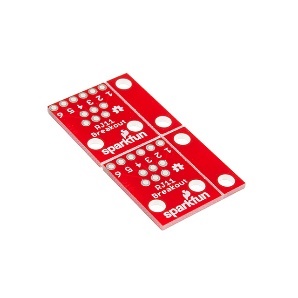
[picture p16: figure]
BOB-14021

RJ11 breakout | | 0.5 | Jack breakout board | Digikey (https://www.digikey.ca/en/products/detail/sparkfun-electronics/BOB-14021/6228638) | 3.05

### Code Structure / Function

The software used is a version of the LipSync code that has been modified to have all pressure and sip/puff functions removed. Other minor changes have also been made, with one of the axis inverted and the deadzone expanded to account for the new sensor location and lower centering force.

https://github.com/makersmakingchange/LipSync/tree/main/Build_Files/Firmware_Files

### RJ11 Jack Retainment

When adding the RJ11 jack to the prototype base, securing the jack to the base proved to be difficult with the print orientation of the base. A snap fit base proved to either be too short to bend properly, or impossible to print due to the overhang, depending on the orientation.

A brainstorming session came up with two alternative ideas, both based around the idea of a sliding track that the jack is inserted in. The first idea was a cotter pin retaining the jack like in the recently redesigned Open Toggle Switch, and the second was a bump in the track that the jack could be forced past but not removed from.

The cotter pin was prototyped first, and found to be so successful that the retaining bump was not developed further due to concerns about being unable to remove the jack for maintenance or repairs of the joystick.

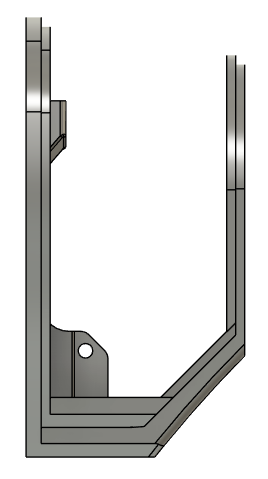
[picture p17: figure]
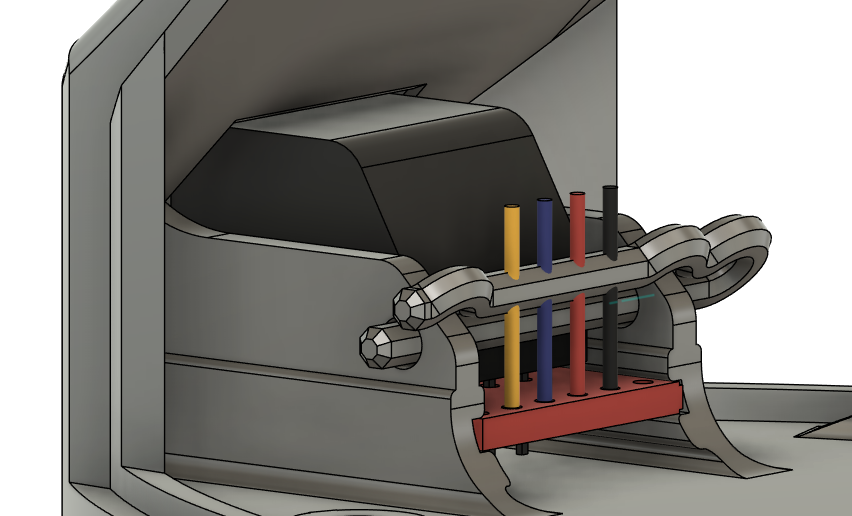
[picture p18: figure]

The assembled jack has been tested for strength, and we have been unable to apply enough force to break the jack out of the 3D printed enclosure.

# Testing

## MVP Verification

In this test, each of the goals, requirements, evaluation criteria, and constraints were evaluated against the MVP Willow joystick, noting if the device passed or failed.

### Test Results

Requirements Testing

Goal | Result | Functional Objective | Result | Non-Functional Objective | Result | Constraint | Result
G01 | Pass | F01 | Pass | NF01 | Pass | C01 | Pass
G02 | Fail | F02 | Pass | NF02 | Pass | C02 | Pass
G03 | Pass | F03 | Pass | NF03 | Pass | C03 | Pass
G04 | Pass | F04 | Pass | NF04 | Fail | C04 | Pass
G05 | Pass | F05 | Pass | NF05 | Pass | C05 | Pass
| | F06 | Pass | NF06 | Fail | C06 | Pass
| | F07 | Pass | NF07 | Pass | C07 | Pass
| | F08 | Pass | NF08 | Pass | C08 | Pass
| | F09 | Pass | | | C09 | Pass
| | F10 | Pass | | | C10 | Pass
| | F11 | Fail | | | C11 | Pass
| | F12 | Pass | | | C12 | Pass
| | F13 | Pass | | | C13 | Pass
| | F14 | Pass | | | C14 | Pass
| | F15 | Fail | | | C15 | Pass
| | F16 | Pass
| | F17 | Pass
| | F18 | Pass
| | F19 | Pass
| | F20 | Pass

## MVP Maker Testing

In this test, various makers from within MMC built Willow Joysticks to distribute to clinicians across North America for testing. This section is less of a formal test, and more of an area to note build feedback on the CAD files. Feedback was also gathered on the Maker Guide instructions, but that feedback was directly implemented in the Maker Guide and outside the scope of the Design Rationale.

### Test Results

Tester 1

- Magnet in the sled does not want to stay in place without both in place, making it very difficult to assemble

Tester 2

- One of the Sled components failed to print
- There is an awkward gap / transition between Joystick Shell and Joystick Base.
- Text on Inner Gimbal is too small to read clearly. Use bigger text or shorter message (e.g., “I1, I2”)
- Assembling small machine screws and nuts to mount sensor board is challenging.

Tester 3

- Magnet in the sled does not want to stay in place without both in place, making it very difficult to assemble

Tester 4

- Difficult to read the text on the inner gimbal bodies
- Inner gimbal does not sit flush on the magnets
- Text on outer gimbal is illegible
- Holes for screws on the magnetic sensor are tight
- Sled has some loose space that allows the gimbal to slide in the x direction
- Add a keyed base to the sled so it can’t be installed backwards
- Change orientation of the octagon so the corners/slots are in the 8 main directions so the joystick can stick in them
- Make the holes for the machine screws in the base bigger
- Magnet in the sled does not want to stay in place without both in place, making it very difficult to assemble

## MVP Characterization Testing

The RJ11 jack was removed from the enclosure, and a hole drilled in the side of the shell. The jack was then fed out the side of the device so that the RJ11 cable would not bend or put extra force on the device if it had to be bend around a section of the jig. The much smaller cables used in the stemma to Dupont cable bend easier and with less force and therefore are less likely to interfere with the force measurements.

Procedure

1. Place the willow orientation jig in the testing jig in the correct orientation for the test that is being performed.
2. Place the willow in the willow orientation jig
3. Gently move the willow along the track until it is just touching the plate of the scale.
4. Extend the calipers until it is just touching the joystick stick.
5. Zero both the scale and the calipers
6. Record the X,Y and Z magnetic sensor readings at 0
7. Extend the calipers by roughly 0.5mm. If slightly over or under this, note down the exact distance.
8. Record the force and magnetic sensor readings
9. Repeat step 7 and 8 until the joystick is bottomed out, which can be determined when the force starts increasing much faster than normal and the magnetic sensor readings barely change
10. Repeat this test for each of the 8 directions of the orientation jig. The orientations are labeled below in figure

During initial testing, three issues that arose were the scale turning off during use if the testing took too long, difficulty getting the willow pressed right against the joystick and scale so both zeros are true zeros, and the orientation jig platform lifting up when the centre of gravity of the willow was closer to the scale. This last issue was solved during the testing process by weighing down the side of the orientation jig that was closest to the calipers. Moving the rollers to the edge of the orientation jig also helps to increase the distance from the center of gravity to the point of rotation.

The values of the magnetic sensor were measured using the default Cartesian example from the TLV493D sensor library, modified to provide a reading every 2500 milliseconds, instead of every 500. When observing the results, it was noticed that when the joystick was in a fixed position, it tended to bounce between three results, generally 0.1mT apart. For example, the readings would bounce between 2.76, 2.86, and 2.96. When writing down the measurements for each position, an attempt was made to take the middlemost reading, although occasionally one of the outlier readings may have been taken.

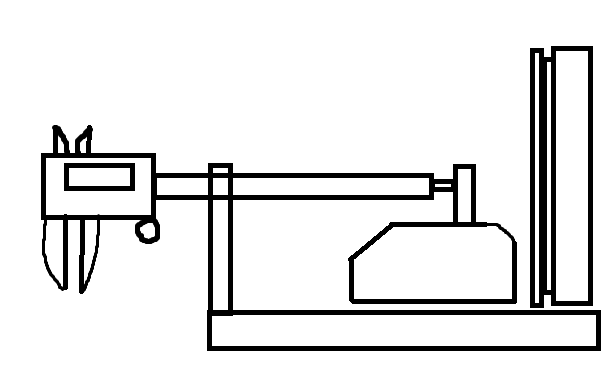
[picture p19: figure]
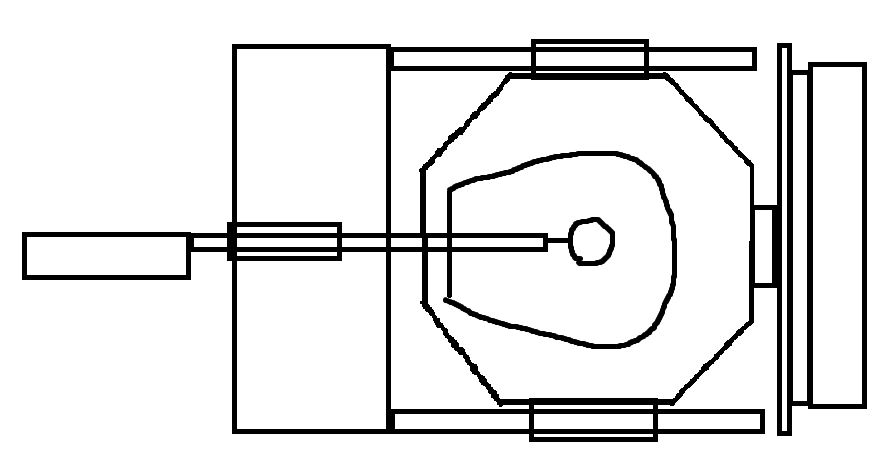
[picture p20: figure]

Figure 3: Top View Sketch of Testing Jig(Right)

Figure 4: Side View Sketch of Testing Jig(Left)

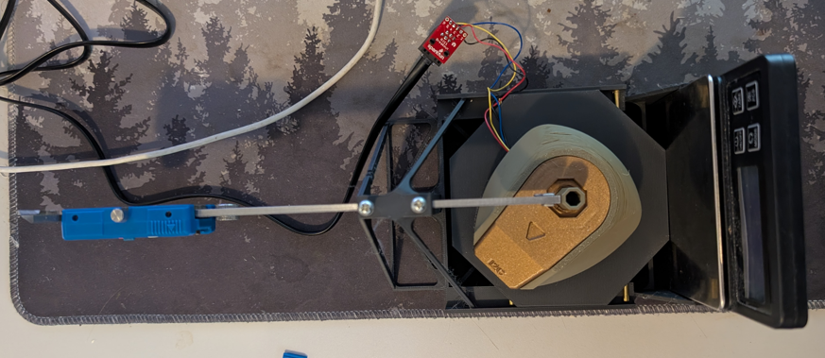
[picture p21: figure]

Figure 5:Top View of Testing Jig

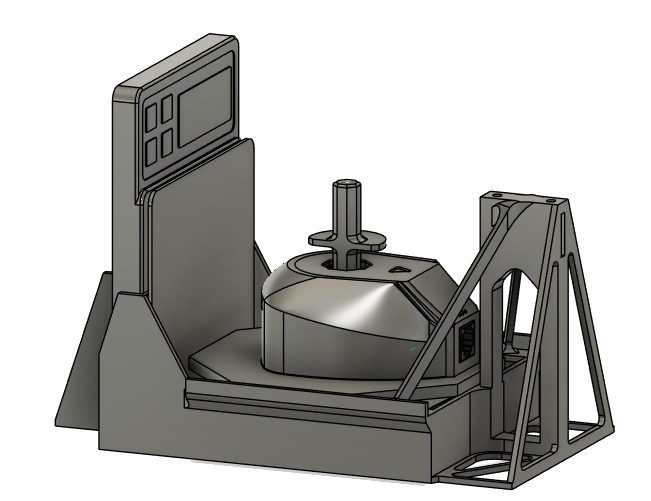
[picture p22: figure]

Figure 6:CAD Render of Testing Jig

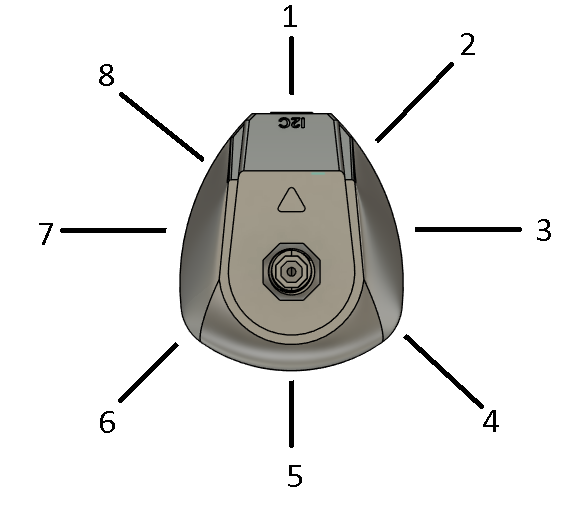
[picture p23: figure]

Figure 7:Directions of Testing

For hysteresis testing, the willow was put into debug mode by opening the serial command menu in the Arduino IDE and entering the command “SETTINGS” followed by “DM,1:1”. This makes the willow output the magnetic sensor readings into the serial monitor. For each of the 8 directions, 5 readings at rest will be taken, then the joystick will be displaced and released, with 5 measurements taken when it is back at rest. This process will be repeated 5 times for a total of 6 sets of 5 readings. This procedure will be repeated for all 8 directions.

### Test Results

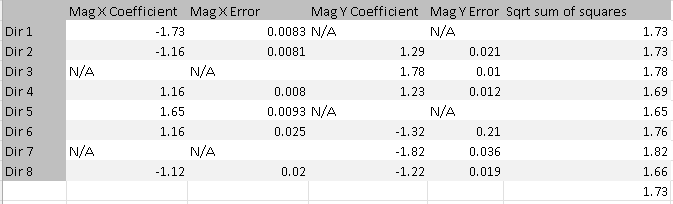
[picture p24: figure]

Figure 8:Directional Magnetic Coefficients

A linear regression analysis was performed on the magnetic sensor readings compared to the displacement angle. It was found that a one degree change in joystick angle corresponded to a 1.73 mT change in magnetic sensor reading.

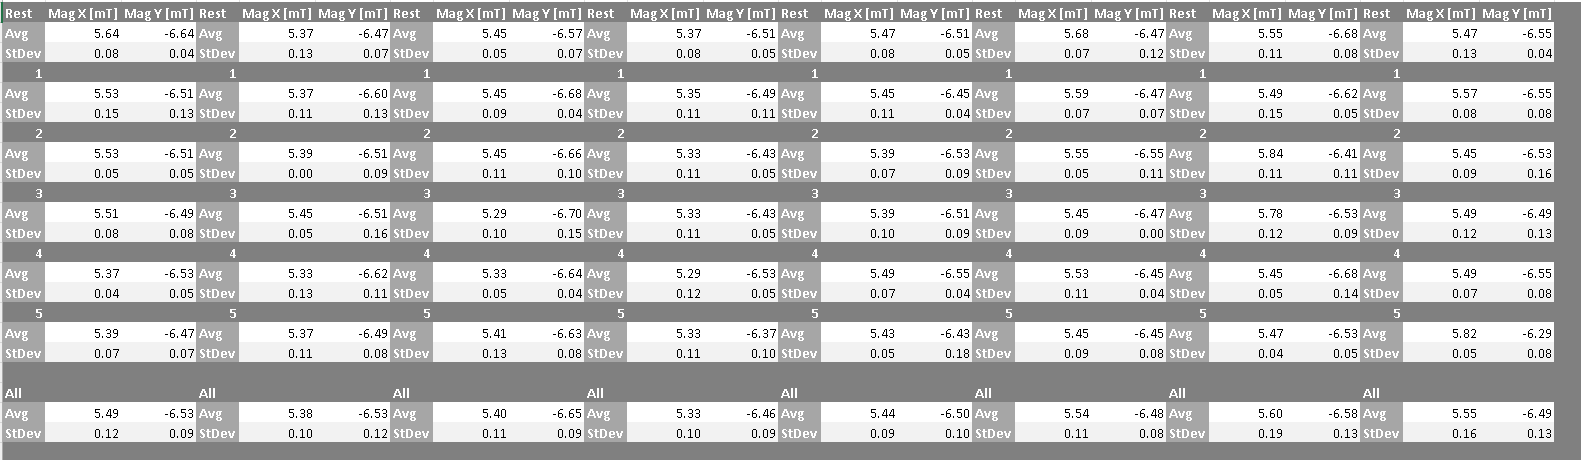
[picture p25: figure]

Figure 9: Magnetic Readings Vs Displacement

When examining the hysteresis data, both the X and Y values fall within a 0.7 mT range.

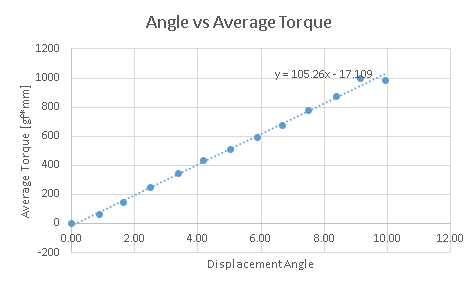
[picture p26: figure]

Figure 10: Angle vs Average Torque

When comparing torque measurements to the displacement angle, a fairly linear relationship of 105-gram force millimeters per angle of displacement emerges. For the 4 different toppers at 5mm of displacement, this corresponds to 22.3g for the 23.5mm tall concave topper, 17.8g for the 29.5 tall convex topper, 18.1 g for the 29mm tall goalpost topper, and 10.7g for the 49mm tall stick topper.

## MVP User Testing

In this test, devices were given to clinicians across the country to test with users and collect feedback. These were MVP devices, that still had some drift while print tolerances and dead zones were being determined.

### TEST 1

After the clinicians had had time to test the devices and become familiar with them, they were interviewed about their experience with the device. They were asked question about the following areas

- Were there any issues with setup/use? Did the joystick slide around, was cable management an issue?
- Was the amount of force okay? Was it too much or too little?
- Was the range of motion ok? Could it be better?
- What did you like about the toppers? What did you dislike?
- Would you prefer this device with the hub or as a standalone? If you would prefer it standalone, how much of the hub functions would you be willing to give up?
- What are your thoughts on the device? What were the users thoughts?
- Was it comfortable to use? If not, what made it uncomfortable?

### Test Results

Clinician 1

- Some drift was noted
- Asked for either the joystick to be lower profile, or some sort of ramp to be added to raise the hand
- Joystick was slippery on the table
- Prefer an alternative to a bolt to hold the topper in place
- Clinicians liked the lilypad topper and one clinician liked using it without a topper, like a roller ball mouse
- Clinician had no issue with setup, although was already familiar with the LipSync
- Clinician complained about cable crossover/cable management issues, although most of these issues were resolved with the addition of a hub stand instead of resting the hub on the table
- Clinician was interested in updating settings through the computer, they were not aware of the serial API but were interested in a webpage that would let them change the settings
- While using the lilypad (The lowest and therefore highest force topper) the force was noted as in the good to high range
- Range of motion is good
- A standalone version without the hub would be nice, but they also want switch inputs

Clinician 2

Clinician 2 did not give any feedback on the Willow

Clinician 3

This device was tested by a clinician, but they will not have a user who will benefit from it until early 2025

- Toppers
  - Convex: Like this topper the most
  - Goalpost: Bolt hole was irritating, and it was a bit too wide for a finger. Maybe make several sizes
  - Concave/Lilypad: Why the cutout? Edge of the cutout digs into the finger. Make it a full circle
  - Stick: Why the ledge?
  - The bolt hole is a concern for crumbs as well as skin build up
- The clinician found it to have a good amount of force
- The clinician liked the range of motion
- The clinician found that it would be useful to have both a hub version and a standalone version.
  - If it was offered as a standalone, make sure to ship it in mouse or gamepad, whatever the user requests
  - While the idea of the hub is nice, some users might not even be able to use the hub so a standalone would be cheaper for them
- The clinician liked that it had a low center of gravity and was not prone to tipping

Clinician 4

- The clinician noted that the device got out of calibration quickly
- The clinician was confused by the hub stand, the quickstart guide did not fully explain the stand
- The clinician had no setup issues, and used the joystick with a mounting arm or a hook and loop patch on a board
- Add more documentation info about the camera mount adaptor
- The clinician liked the range of motion and noted that it was just enough for games to differentiate between walking and running
- The clinician liked the ergonomics and thought adding a ramp to support the hand would be a valuable option
- The clinician like the hub, and had never seen a LipSync before. They especially liked that the button timing allowed users to do 3 different inputs based on just one switch. They mentioned that some clients only can use 2 inputs, so 1 joystick and 1 switch is their limit, and this allows multiple outputs from the single input.
  - Clinician was interested in remapping the outputs to put the most useful outputs on the same switch input.

## Printer Testing

To this point, all the design work for the Willow has been done on a Bambu Labs P1S printer. This is a relatively high end printer, with highly tuned profiles and automatic bed leveling. Since many of the important features of the gimbal are on the surface that contacts the print bed, and they often have very little contact area with the bed, the decision was made to do a test print with an original Ender 3, with no bed leveling or other advanced features.

When trying to assemble the printed parts, it was found that any degree of elephant’s foot from the bed not being appropriately leveled caused the assembly of the gimbal to be extremely difficult, if not almost impossible. However, there were no issues with parts lifting off of the bed due to low contact area.

Because of this difficulty assembling if the bed is not appropriately leveled, it is recommended that only printers with an automatic bed leveling be used when printing a Willow.

# Detailed Design

Action items leaving stage 3

- Enclosure refinement
- Wrist ramp. 3D printed or foam
- Replace topper bolt system
- Look into toppers more
- Add feet to enclosure base
- Determine ideal dead zone
- Integrate results of linearity testing into code
- Test print of gimbal on bad printer

## Topper System

The test MVP joystick shipped with 4 toppers, a concave topper with a slot cut out for a finger, a convex topper, a goalpost topper, and a stick topper. The clinicians who tested the device had a variety of opinions on the topper, both on the size and shapes of toppers available, and the bolt system used to attach the toppers to the joystick.

The bolt topper system had two main problems that were noted, cleanliness/comfort, and swapability. It was noted that the hole in the topper that the bolt passed through was both uncomfortable to the user as well as a trap for things like crumbs and flakes of skin. The depth of the hole also required a small narrow screwdriver to reach the bolt, which makes it difficult to change toppers during use.

In the discussion about this, it was decided to replace the bolt topper system with something more clean, comfortable, and convenient. Ideas such as a gutter lock, snap fit, and threaded insert were discussed.

The requirements for a replacement system are as follows

- The topper must be orientable (a topper such as the goalpost with an orientable feature must be able to be reliably oriented correctly on the joystick)
- The topper attachment system must not require tools to swap the toppers

The criteria for a replacement are as follows

- The topper attachment system should not make the topper less comfortable or more difficult to clean
- The topper should have minimal parts
- The topper should be durable
- The topper should require minimal force to install
- The topper should be easily printable

### Gutter Lock

A gutter lock system would have the toppers with two tabs, and two corresponding slots on the gimbal. The topper can be freely inserted down the gimbal, then turned 90 degrees to prevent it from being removed. The tab and channel system would have a detent to hold the topper in the twisted position.

Pros

- The tabs provide the force keeping the topper in place, so the force required to twist it in can be much lower than the force holding the topper in place
- No tools required

Cons

- Existing toppers print in two different orientations, the tabs would need to be designed to print in both orientations.
- Potential for topper to delaminate and leave the tabs stuck in the gimbal

### Snap Fit

The snap fit topper would have a set of detents on the topper, and a set of tabs on the gimbal. The

Pros

- Simple insertion and removal
- No tools required

Cons

- Existing toppers print in two orientations, so the detents would need to be printable in two orientations
- The force to insert the topper and the toppers resistance to being pulled out are the same.

### Threaded Topper

A threaded topper would come in one of two forms, a threaded topper or a threaded topper collar. The threaded topper would have a threaded connection on the base of the topper, and a matching interior thread on the gimbal. The topper would then screw into the gimbal.

A topper collar would still have the threads on the gimbal, but the topper itself would not have threads. Instead, it would have a lip or some other feature that a threaded retaining ring would sit over. This threaded collar would thread into the gimbal and provide the clamping force to hold the topper in place.

Pros

- A secure, robust connection
- No tools required
- Holding force is distributed along the length of the entire connection

Cons

- No real control over the orientation of the topper if it is just threaded in
- If using a threaded collar, additional vertical and horizontal clearance is required to allow access to the collar, and it has the potential to interfere with the range of motion and force of the gimbal

After reviewing the pros and cons of each, the gutter lock system provides the most secure connection without requiring tools and with minimal changes required to the gimbal. The twist tabs allow for them to resist more force than it takes to insert them, and it allows them to be oriented accurately instead of stopping when the thread bottoms out.

A modified version of the gimbal and the lilypad topper were created to test this attachment method. The diameter of the inner section of the gimbal had to be reduced by 3mm to create an area for the tabs on the gimbal to pass through and twist into. This means that the diameter of the toppers also had to be reduced to fit into the gimbal. This reduction in diameter also reduces the print bed area which poses a danger when trying to print the toppers with a wider top such as the lilypad topper. The print bed area was low enough that the slicing software automatically added a brim around the topper which also affects the tolerances. The gutter lock system itself worked well, although some refinement of the tolerances is needed. The test did not have the retaining detent, but with some force it inserts in the gimbal and twists a full 90 degrees.

With the print orientation of the toppers and the gimbal, the retaining tabs can be added to the gimbal, and the detents to the topper.

After printing a gimbal with the gutter lock and tabs, and a topper with the detents, it was found that the systems works well. The slicer added a brim to the topper to allow it to print without being knocked over by the print head, and after the brim was cleared off the topper it fit well in the gutter lock of the gimbal. The tab and detent system had a noticeable click once fully rotated and held its position well.

There are concerns about the longevity of the tab in the gimbal with the possibility that it may get worn down over time. The idea of placing the detent on the gimbal so that the tab that wears down is on the topper which is more easily replaced was examined, but running the detent along the entire length of the slot is more difficult and will wear down faster that passing the detent over ~1mm of plastic on the topper.

After ~20 times inserting and removing the topper, the force required became lower and lower until there was almost no click or noticeable resistance when fully turning the topper. However, after printing a new topper the force required returned to normal, showing that the wear occurs mostly on the much more easily replaceable topper, rather than the inner gimbal itself.

### Topper System Decision

After reviewing the gutter lock system and the cons of the other two proposed but unmodeled designs, the decision was made to proceed with the gutter lock system.

## Topper Options

The clinician that tested the toppers that came with the Willow had a range of feedback on topper sizes, shapes, and comfort. During the review of the feedback, it was decided to review the topper options to provide more customizable and useful options.

The idea of providing life size images of the toppers in the documentation was discussed, as well as parametric toppers that users customize. The idea of a topper that is compatible with the Xbox Adaptive Thumbstick toppers was also discussed.

Reviewing the topper option for the joysticks currently in the library, there seems to be 6 common types of toppers. The shapes of toppers found in the MMC library include ball, concave, convex, goalpost, stick, and ring. These toppers either come in one size, or in a small, medium, and large size. Earlier in the design process the possibility of reusing toppers from the other joysticks was ruled out, but the choices of style and size of toppers can be used for the design of toppers for the Willow. The larger sizes of toppers would most likely not be feasible due to the weight, but the smaller sizes can likely be duplicated in the Willow.

### Topper Selection

When reviewing the gutter lock system on the Willow, the decision was made to proceed with the topper options that were chosen for the MVP prototype, converted to work with the gutter lock system and with the feedback from the users incorporated, such as making the goalpost topper wider and removing the groove from the concave lily pad topper.

The decision was also made to create a topper that is based on one of the Xbox adaptive thumb sticks (https://xboxdesignlab.xbox.com/en-ca/accessories/adaptive-thumbstick-toppers-for-xbox-controllers), designed to have a large amount of surface area for heat mouldable plastic pellets to adhere to allow clinicians and users to create their own custom topper without needing to know 3D modelling and printing.

Additionally, the 3D design file for a blank topper with just the gutter lock and stem was made available so that makers can create their own toppers that are fully compatible with the Willow.

## Hub

One of the goals of the testing feedback was to determine the output architecture of the Willow. While a number of options were considered, the two primary categories that they fell into was a hub, or a standalone joystick.

The version of the Willow that was shipped to testers used a reprogrammed LipSync Hub to provide switch inputs, visual and audio feedback, and contained the microcontroller for the device. The testers were asked if they liked the hub, or if they would prefer a standalone device, and what they would give up to get to a standalone device.

Every clinician that tested the device liked the hub and the options that it provided, but said that they would also be interested in a standalone version. The testers that specialized in computer access especially liked the built in switch access, as well as having multiple computer outputs from a single switch input with different press timings. The testers who focused on accessible gaming did not mention switch inputs, likely due to using intermediary systems such as the Xbox Accessible Controller (XAC) that already have switch inputs. A point that was raised by one tester is that some users may not be able to use the hub to change settings so a standalone version would prevent them from having to spend extra money on a hub that they cannot use.

The LipSync Hub used with the Willow was programmed with a modified version of the LipSync code. Since the Willow works on the same principle as the LipSync, the pressure sensing parts of the LipSync code could be removed and the axes directions inverted to create a working version of the Willow that maintains the input, output, and feedback options of the LipSync.

The results of this testing show two different use cases for the Willow, the complete solution and the solution component. The complete solution is used in computer access situations, where the Willow Joystick, Willow Hub, and up to three switches are used to control a device such as a computer or mobile phone. The solution component is used in accessible gaming solutions where the Willow Hub and Willow Joystick are connected to another device that has other accessible technology connected to it, such as a XAC or a computer with a rocket switch interface.

The complete solution Willow requires the switch inputs of the Willow Hub and is improved by the user feedback options that the hub provides. The solution component Willow does not require the switch inputs of the Hub, but is not made worse by having them available. The main downside to using the Willow Hub in a solution component use case is the additional cost of building the Hub, which costs ~$110 CAD in addition to the ~$50 CAD joystick. A standalone joystick is estimated to cost ~$70-80, depending on what inputs and outputs the joystick has.

Considering the different use cases for the willow and the two possible paths for a standalone or hub Willow, the recommendation is to carry forward with the hub version of the Willow. It already exists, with a working code base that needs minimal changes to get it release worth. It provides a large number of feedback and input options while keeping the joystick simple enough to be potentially compatible with any of the i2c compatible hubs in the MMC library.

However, there is a case for a standalone version of the Willow for users looking for a low cost option, users who have no need for the number of inputs/outputs the Willow provides, or users who are using the Willow as part of a larger accessibility solution. The physical gimbal system itself would not need to be changed, but a new enclosure would need to be designed to allow for the microcontroller and possible a small number of input switches or output lights, as well as a modification of the existing codebase or creation of a new codebase.

## Joystick Height

One of the most common complaints raised about the Willow was the height of the joystick. Even after redesigning it from the LipSync gimbal to reduce the heigh as much as possible, the clinicians still felt that it was too tall. This feedback about heigh also came with a request for a ramp of some sort to raise the height of the user’s hand relative to the joystick.

Enclosure modification One option for raising the users hand relative to the Willow is a modified enclosure that provides a more gentle slope for the hand to rest on. This slope can either be build into the enclosure, or an optional enclosure add on as seen on the Aspen Joystick. However, the customizability is limited by the need to fit the gimbal or the existing enclosure, and it also is limited to only be used with the Willow joystick.

Foam ramps to raise the user’s hand relative to the joystick can be purchased commercially, or DIYed by a clinician out of foam. A parametric 3D printable ramp will also be designed and added to the project files for a easy to customize low effort way to elevate the user’s wrist.

## Anti-Slip Feet

One of the most consistent pieces of test feedback received was that the joystick tended to slip and slide on the table when used. The addition of non slip feet was already planned, and this feedback increased the priority of this change.

The primary challenge with adding non slip feet is finding an appropriate foot to use. They are commonly available at dollar stores, but the varying diameters and thicknesses of the feet make it difficult to add design features to the base to accommodate them. After searching on Digikey, a suitable option was found. The foot was both small and thin, as well as available to be purchased individually instead of in bulk. A sample set was ordered to test the actual non slip ability of the feet, and they were found to be suitably resistant to sliding.

The design of the base was modified to allow the addition of the feet. The length of the enclosure had to be increased to allow clearance for the feet when the camera mount adaptor is attached.

The feet were initially placed to cover the screw holes on the base of the enclosure, but it was found that when placed over the screw holes, the spacing required for the camera mount adaptor cased the joystick to be prone to rocking when a strong force is applied to the ‘southeast’ or ‘southwest’ direction of the joystick.

To limit the tipping, a variety of solutions were considered. These solutions were a rim around the base in addition to the feet, widening the base so that there is room to have the feet beside the camera adaptor, replacing the feet with a piece of Dycem, rotating the camera mount adaptor to make space for the feet, and a second adaptor that bolts onto the camera adaptor nuts to add feet that can be removed and replaced with the camera mount adaptor.

Adding a rim around the base of the willow would help prevent rocking, but would need to be precisely the right height to allow the feet to contact the surface to limit slipping, while also not allowing the device to tip. This rim height would be dependent on the feet used, so if the maker used anything other than the feet linked in the BoM, the rim would not work.

Widening the base to move feet to outside of camera adaptor was tested, and it was found that it greatly increased the size of the enclosure, and created dead space inside the enclosure. This increased size restricts positioning options and may make the device more cumbersome for the user.

Dycem is a frequently used option that provides non slip with minimal added height, but has the downside of requiring the purchase of an entire roll. This would be a good option for therapists or other AT professionals who may have it on hand already, but could be cost prohibitive for a maker who does not already have a roll.

The idea of rotating the camera mount 90 degrees to provide room for the feet was examined but discarded after it was discovered that it would interfere with the RJ11 jack.

Finally, the idea of creating a separate foot, similar to the one used in the testing jig was proposed. The foot would have slots for the non slip pads, and bolt to the same embedded nuts that the camera adaptor does. This would allow for the foot to be removed when the camera adaptor is needed, and also allows for Dycem to be used instead of the foot if the user has it on hand.

After printing the non slip foot, it was found that it raised the height of the joystick by 4mm, and did not have any tipping issues under normal or forceful use.

# Design Validation Plan

## Executive Summary

## Test Plan

Due to the thoroughness of the testing done in Stage 3, the testing in this section will be focused on the changes made in Stage 4 as a result of the feedback gathered.

### Evaluate Final Product vs Initial Requirements, Goals, and Constraints

- Evaluate each of the goals, functional requirements, nonfunctional requirements, and constraints against the current design
- If any fails, explain why

### Evaluation of Gutter Lock Toppers

- Get 3 makers to do a test print and get feedback
- Determine the approximate force required to lock the topper in place with a fresh print
- Get clinician feedback on toppers

### Evaluation of Non-Slip Base

- Determine how much force is required to cause the device to slip on a smooth desk surface
- Determine how much force is required to tip the device when applied to each topper
  - Test for each of the four ‘lines’ between the nonslip feet

### Evaluation of Wrist Ramp

- Get 3 makers to do a test print and get feedback
- Change the parametric settings ~25% to see if any design features are prone to breaking
- Get a test print to a clinician for feedback

## Test Results

### Evaluate Final Product vs Initial Requirements, Goals, and Constraints

### Evaluation of Gutter Lock Toppers

### Evaluation of Non-Slip Base

### Evaluation of Wrist Ramp

# Finalized Willow

The final version of the Willow that is being published as V1.0 consists of two separate components. The first component is the Willow Joystick, and the second component is the Willow Hub.

The Willow hub is almost identical to the LipSync hub, with the only difference being the label on the enclosure and the firmware that it is running. The firmware is a modified version of the LipSync firmware that has all the sip and puff functionality removed.

The Willow Joystick uses the same magnetic gimbal concept as the LipSync, but with the sip and puff sensors removed, and the gimbal redesigned to make it lower profile. The mouthpiece of the LipSync has been replaced by a set of gutter lock toppers.

Goal | Result | Functional Objective | Result | Non-Functional Objective | Result | Constraint | Result
G01 | Pass | F01 | Pass | NF01 | Pass | C01 | Pass
G02 | Fail | F02 | Pass | NF02 | Pass | C02 | Pass
G03 | Pass | F03 | Pass | NF03 | Pass | C03 | Pass
G04 | Pass | F04 | Pass | NF04 | Fail | C04 | Pass
G05 | Pass | F05 | Pass | NF05 | Pass | C05 | Pass
| | F06 | Pass | NF06 | Fail | C06 | Pass
| | F07 | Pass | NF07 | Pass | C07 | Pass
| | F08 | Pass | NF08 | Pass | C08 | Pass
| | F09 | Pass | | | C09 | Pass
| | F10 | Pass | | | C10 | Pass
| | F11 | Fail | | | C11 | Pass
| | F12 | Pass | | | C12 | Pass
| | F13 | Pass | | | C13 | Pass
| | F14 | Pass | | | C14 | Pass
| | F15 | Pass | | | C15 | Pass
| | F16 | Pass
| | F17 | Pass
| | F18 | Pass
| | F19 | Pass
| | F20 | Pass

# Opportunities for Improvement

### Physical Component / Enclosure

There are several opportunities for improvement with the 3D printed parts of the Willow.

- A custom camera mount adapter could be created that blends better with the enclosure
- The enclosure could be modified with a built-in optional weight to remove the need for a nonslip foot.
- The M3 nut captures on the base could be redesigned to be more in line with the nut captures used on the existing OpenAT joysticks
- Modify the toppers to have wrench flats and add a 3D printable wrench to the build files.
- The indents for the feet on the nonslip pad could be made larger to accommodate a larger variety of non slip feet.

### Code Structure / Function

The primary opportunity for code improvement is to merge the code base of the willow and the LipSync so that changes to one do not need to be duplicated to the other and to allow the hubs to be interchangeable without needing to reprogram them.

© 2024 by Neil Squire. This work is licensed under the CC BY SA 4.0 License: http://creativecommons.org/licenses/by-sa/4.0 Files available at https://github.com/makersmakingchange/Willow-Joystick Page 1 of 1

V0.1 | September 2024 Willow Joystick Design Rationale

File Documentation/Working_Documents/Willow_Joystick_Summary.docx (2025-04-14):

# Overview

After developing the LipSync, an opportunity arose to take the magnetic gimbal system and develop it further to create a low force addition to the MMC joystick library. The Willow uses a reprogrammed LipSync hub, and a smaller version of the LipSync gimbal with the pressure sensors removed.

The Willow has files available for 7 different toppers, as well as the design file to create your own custom topper. It also has files for 4 different wrist ramps with an editable design file, and a hub stand to keep the hub screen visible. Finally, it also comes with files for two different mounting adaptors for the joystick, as well as a nonslip base attachment.

The Willow is compatible with a range of host devices that are able to support a USB Mouse, a USB Gamepad and/or a Bluetooth Mouse. Compatible devices include PC and Mac computers and laptops, Android, iOS, and Windows smartphone and tablets, and the Xbox Adaptive Controller.

The Willow is Open Assistive Technology (OpenAT) and is certified as Open Source Hardware by the Open Source Hardware Association under the OSHWA UID CA000062 (https://certification.oshwa.org/ca000062.html). Under the terms of the open source hardware licenses, the Willow may be built, used, and improved by anyone.

Product Information

## Product Name

Willow Joystick

## Device Category

Mark any relevant categories with an “X”:

| Adapted Toys
| Aids for Daily Living (ADL)
| Assistive Switches
| Communication Aids (AAC)
X | Computer Access
| Environmental Controls
X | Gaming
| Keyguard
| Kits
| LipSyncs
| Mounting
| Recreation and Leisure
| Seating and Positioning
| Switch Interfaces
| Writing Aids

## User Value Statement

The Willow joystick allows users with low force/range of motion to access their digital devices for cheaper than a commercial option.

## Designer

Neil Squire Society

# Device Information

## Overview

The Willow is made up of the Willow Joystick and the Willow Hub. The Joystick is the primary user interface and contains a low-force Hall-Effect joystick. The Hub has a display that provides a graphical interface for independently adjusting settings, as well as it provides the connection to the host device and up to three external assistive switches with 3.5 mm jacks.

The Willow uses a modified version of the LipSync firmware and is compatible with a range of host devices that can support a USB Mouse, a USB Gamepad and/or a Bluetooth Mouse. Compatible devices include PC and Mac computers and laptops, Android, iOS, and Windows smartphone and tablets, and the Xbox Adaptive Controller.

The joystick requires 25 grams of force to operate and comes with 7 different swappable toppers. It has adaptors for both ¼-20 mounting arms and RAM B ball mount arms and has an optional nonslip base for use on a table. There is also a modifiable wrist ramp to help raise a user’s wrist while using the joystick.

## Disability Type

Select one or more disability types and mark with an “X”:

| Agility / Dexterity
X | Arthritis
| Cognitive
| Hearing
| Mobility
| Pain
X | SCI
| Vision
| Other

## Disability Type Description

The Willow is designed for users with low range of motion/low force, such as users with Spinal Muscular Atrophy.

## How To Use

The joystick is plugged into the hub, and up to three assistive switches can also be connected. The hub can be connected to a device through either a direct USB connection, or through Bluetooth.

Moving the joystick moves the connected cursor in mouse mode or the gamepad joystick in gamepad mode. The connected assistive switches can be used to perform mouse clicks, scrolls, and drags in mouse mode, or act as gamepad buttons in gamepad mode.

The hub menu allows the user to change settings such as light brightness, cursor speed, and scroll speed.

Full instructions can be found in the quickstart guide or the user guide.

## Estimated Cost

The estimated material cost of the device for a single build:

| $0 - $10
| $11 - $25
| $26 - $50
| $51 - $100
X | $101 - $250
| $250+

## Attribution

Designers:

- Brad Wellington, Neil Squire Society / Makers Making Change.
- Stephen Moyer, Neil Squire Society / Makers Making Change.
- Josie Versloot, Neil Squire Society / Makers Making Change.
- Tyler Fentie, Neil Squire Society / Makers Making Change.
- Jake McIvor, Neil Squire Society / Makers Making Change.

# Maker Information

## Project Skills

Mark the required project skills with an “X”:

X | 3D Printing
X | Custom PCB
X | Electronics
| Laser Cutting
| Mechanics
| Software
X | Soldering
| Woodworking
| Other

## Skills Description

Making the hub primarily involves soldering components to a custom PCB, and making the joystick involves assembling 3D printed components to make the gimbal.

## Tools Needed

X | 3D Printer
X | Common Hand Tools
| Common Power Tools
| Laser Cutter
X | Soldering Iron
| Specialized Tooling

## Print time (hrs)

9

## Assembly time (hrs)

8

## Build Instructions

The enclosure and most of the joystick parts are 3D printed, the electrical parts are ordered from Digikey or Mouser, and the PCB is custom ordered using the provided files.

The hub is mostly soldering, then assembling the enclosure around the finished circuit board. The joystick involves assembling a gimbal using magnets, 3D printed parts, and a sensor board. This requires some dexterity to attach bolts while holding everything together.

The firmware files are included, and just require the requisite libraries to be installed then the firmware can be compiled and installed.

Full instructions can be found in the maker guide.

## Download Link

github.com/makersmakingchange/Willow-Joystick/archive/refs/heads/main.zip

## Project Link

github.com/makersmakingchange/Willow-Joystick

# License

## License

Everything needed or used to design, make, test, or prepare the Willow Joystick is licensed under the CERN 2.0 Weakly Reciprocal license (CERN-OHL-W v2) or later .

All software is under the GNU General Public License v3.0 (GPL-3.0).

Accompanying material such as instruction manuals, videos, and other copyrightable works that are useful but not necessary to design, make, test, or prepare the Willow Joystick are published under a Creative Commons Attribution-ShareAlike 4.0 license (CC BY-SA 4.0) .

© 2025 by Neil Squire. This work is licensed under the CC BY SA 4.0 License: http://creativecommons.org/licenses/by-sa/4.0 Page 1 of 2

V1.0 | April 2025 Willow Joystick Summary

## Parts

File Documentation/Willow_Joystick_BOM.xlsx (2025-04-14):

Device: | Willow Joystick
Version: | V1.0.0
Last Updated: | 2025-03-07
 |  |  |  |  |  |  |  | Total filament (g) |  | Unit Cost | Total Estimated Cost | Build Cost
 |  |  |  |  |  |  |  | 169 |  | $135.24 | $179.04
ID | Commercial Parts |  |  |  |  |  |  |  |  | $124.84 | $144.64
 | Part | Description |  | Manufacturer | Supplier | QTY / Device | QTY / PKG | PKGs | $/ PKG | $ / Device | Total Estimated Cost |  | Link
Joystick Parts
 | TLV493D | Adafruit TLV493D Triple-Axis Magnetometer - STEMMA QT / Qwiic | Joystick | Adafruit | Digikey | 1 | 1 | 1 | $8.53 | $8.53 | $8.53 |  | https://www.digikey.ca/en/products/detail/adafruit-industries-llc/4366/10481837
 | Bearing | 0.250" ball bearing, 1/4" ID, 0.5" OD | Joystick | Mechatronics Bearing Group | Digikey | 4 | 1 | 4 | $3.41 | $13.64 | $13.64 |  | https://www.digikey.ca/en/products/detail/mechatronics-bearing-group/DDRI814ZZRA3P25LY121/9608362
 | Magnet | Cylindrical magnet, 8 mm OD, 2.5 mm thick | Joystick | Radial Magnet, Inc. | Digikey | 3 | 1 | 3 | $1.18 | $3.54 | $3.54 |  | https://www.digikey.ca/en/products/detail/radial-magnets-inc/9029/5218824
 | QWIIC-150 to Male Headers | JST SH 4-PIN TO PREMIUM MALE HEA | Joystick | Adafruit | Digikey | 1 | 1 | 1 | $1.39 | $1.39 | $1.39 |  | https://www.digikey.ca/en/products/detail/adafruit-industries-llc/4209/10230003
 | RJ11 Breakout Board | RJ11 Breakout | Joystick | SparkFun Electronics | Digikey | 1 | 2 | 1 | $3.01 | $1.50 | $3.01 |  | https://www.digikey.ca/en/products/detail/sparkfun-electronics/BOB-14021/6228638
 | RJ11 Cable | Modular Cable Plug to Plug 6p6c (RJ11, RJ12, RJ14, RJ25) 7.00' (2.13m) Unshielded | Joystick Cable | Assmann WSW Components | Digikey | 1 | 1 | 1 | $3.94 | $3.94 | $3.94 |  | https://www.digikey.ca/en/products/detail/assmann-wsw-components/AT-S-26-6-6-B-7-R/1972588
 | Modular Connector Jack | Jack Modular Connector 6p6c (RJ11, RJ12, RJ14, RJ25) 90° Angle (Right) Unshielded Cat3 | Joystick | TE Connectivity AMP Connectors | Digikey | 1 | 1 | 1 | $1.45 | $1.45 | $1.45 |  | https://www.digikey.ca/en/products/detail/te-connectivity-amp-connectors/5555165-1/769566
 | Non Slip Bumper | Adhesive non slip bumper | Joystick | Bumper Specialties Inc. | Digikey | 8 | 1 | 8 | $0.18 | $1.44 | $1.44 |  | https://www.digikey.ca/en/products/detail/bumper-specialties-inc/BS34CL12X25RP/13213600
 | M3 Bolt | PAN HEAD SCREW_M3 X 8MM CROSS SL | Joystick | Würth Elektronik | Digikey | 2 | 1 | 2 | $0.90 | $1.80 | $1.80 |  | 97790803111 Würth Elektronik | Hardware, Fasteners, Accessories | DigiKey
 | M3 Nut | HEX NUT 0.217" STEEL M3 | Joystick | Keystone Electronics | Digikey | 2 | 1 | 2 | $0.28 | $0.56 | $0.56 |  | https://www.digikey.ca/en/products/detail/keystone-electronics/4708/4499301
Hub Parts
 | QWIIC-100 | Qwiic JST SH 4-pin Cable - 100 mm | Hub | Adafruit | Digikey | 1 | 1 | 1 | $1.39 | $1.39 | $1.39 |  | https://www.digikey.ca/en/products/detail/adafruit-industries-llc/4210/10230021
 | Seeed Studio Xiao nrf52840 | Microcontroller | Hub | Seeed Studio Technology Co., Ltd. | Digikey | 1 | 1 | 1 | $15.85 | $15.85 | $15.85 |  | https://www.digikey.ca/en/products/detail/seeed-technology-co.,-ltd/102010448/16652893
 | Male Headers for Xiao | 7-pin male headers for microcontroller | Hub | Seeed Studio Technology Co., Ltd. | Digikey | 2 | 5 | 1 | $0.37 | $0.15 | $0.37 |  | https://www.digikey.ca/en/products/detail/seeed-technology-co-ltd/102010490/19176770
 | Mono Switch Jacks | Mono switch jacks | Hub | CUI Devices | Digikey | 3 | 1 | 3 | $2.29 | $6.87 | $6.87 |  | https://www.digikey.ca/en/products/detail/cui-devices/SJ1-3535NG/738699
 | Tactile switches | Tactile switches for controls | Hub | Omron | Digikey | 2 | 1 | 2 | $1.02 | $2.04 | $2.04 |  | https://www.digikey.ca/en/products/detail/omron-electronics-inc-emc-div/B3F-5050/368377?s=N4IgTCBcDaIEIGYBiBaArABkyAugXyA
 | 7 Pin Female Headers | 7 position female headers | Hub | Sullins Connector Solutions | Digikey | 2 | 1 | 2 | $0.88 | $1.76 | $1.76 |  | https://www.digikey.ca/en/products/detail/sullins-connector-solutions/PPTC071LFBN-RC/810146
 | 4 Pin Male Headers | 4 Pin Male Headers | Hub | Sullins Connector Solutions | Digkey | 1 | 1 | 1 | $0.19 | $0.19 | $0.19 |  | https://www.digikey.ca/en/products/detail/sullins-connector-solutions/PRPC004SAAN-RC/2775250
 | LCD feedback screen | Monochrome 1.3" 128x64 OLED graphic display - STEMMA QT / Qwiic | Hub | Adafruit | Digikey | 1 | 1 | 1 | $30.47 | $30.47 | $30.47 |  | https://www.digikey.ca/en/products/detail/adafruit-industries-llc/938/5774238
 | Buzzer PS1240 | Piezo Buzzer PS1240 | Hub | TDK | Digikey | 1 | 1 | 1 | $0.92 | $0.92 | $0.92 |  | https://www.digikey.ca/en/products/detail/tdk-corporation/PS1240P02BT/935924
 | 5MM Red LED | Diffused 5MM Round T/H Red LED | Hub | Würth Elektronik | Digikey | 3 | 1 | 3 | $0.26 | $0.78 | $0.78 |  | https://www.digikey.ca/en/products/detail/w%C3%BCrth-elektronik/151051RS11000/4490012
 | LED Resistors | 68 Ohm Resistor, 1/4W | Hub | YAGEO | Digikey | 3 | 1 | 3 | $0.16 | $0.48 | $0.48 |  | https://www.digikey.ca/en/products/detail/yageo/CFR-25JB-52-68R/2832
 | Speaker Resistor | 100 Ohm Resistor | Hub | YAGEO | Digikey | 1 | 1 | 1 | $0.14 | $0.14 | $0.14 |  | https://www.digikey.ca/en/products/detail/yageo/MFR-25FBF52-100R/12795
 | Capacitor | 10 µF Ceramic Capacitor | Hub | KEMET | Digikey | 1 | 1 | 1 | $1.01 | $1.01 | $1.01 |  | https://www.digikey.ca/en/products/detail/kemet/C430C106K3R5TA/6685941
 | Qwiic Adapter Board | Sparkfun Qwiic Adapter | Hub | SparkFun Electronics | Digikey | 1 | 1 | 1 | $2.34 | $2.34 | $2.34 |  | https://www.digikey.ca/en/products/detail/sparkfun-electronics/DEV-14495/7942483?s=N4IgTCBcDaICIFEBqBaAjAFgwTgKwgF0BfIA
 | M2.5 Nut | HEX NUT, NATURAL, NYLON, M2.5 X | Hub + Joystick | Essentra Components | Digikey | 9 | 1 | 9 | $0.19 | $1.71 | $1.71 |  | https://www.digikey.ca/en/products/detail/essentra-components/04M025045HN/9677099
 | M2.5 Screw - 8 mm length | PAN PHILLIPS SCREW, M2.5X0.45 T x 8 mm Long | Hub + Joystick | Essentra Components | Digikey | 9 | 1 | 9 | $0.20 | $1.80 | $1.80 |  | https://www.digikey.ca/en/products/detail/essentra-components/50M025045P008/11638585
 | Light Pipe 0.250" | Light Pipe | Hub + Joystick | Dialight | Digikey | 1 | 1 | 1 | $1.66 | $1.66 | $1.66 |  | https://www.digikey.ca/en/products/detail/dialight/51513030250F/4965201
 | No.4 Screw x 3/8in | SHT MTL SCREW PAN PHIL #4 | Hub + Joystick | Serpac | Digikey | 6 | 1 | 6 | $0.63 | $3.78 | $3.78 |  | https://www.digikey.ca/en/products/detail/serpac/6005/307599
 | T-Nut | 1/4-20 T-nut x 5/16" length | Hub + Joystick | PowerTec | Amazon | 2 | 50 | 1 | $18.83 | $0.75 | $18.83 |  | https://www.amazon.ca/gp/product/B07NCXNKJR
 | USB C cable - 6 ft | USB C to USB A cable for microcontroller | Hub Cable | Amazon | Amazon | 1 | 1 | 1 | 12.95 | $12.95 | $12.95 |  | https://www.amazon.ca/dp/B01GGKYN0A?_encoding=UTF8&ref_=cm_sw_r_cp_ud_dp_R153PNRRHEZ23HBEP492&th=1
 | 3D Printed Parts |  |  |  |  |  |  | 178 |  | $4.40 | $4.40
 | Part | Description | Filament Type | Filament | Color | QTY / Device | Mass (g) / Part | Total Mass | $ / kg | $ / Device | Total Estimated Cost |  | Link
 | Willow_Joystick Base.stl | Main body of joystick | PLA |  | Any | 1 | 27 | 27 | $25.00 | $0.68 | $0.68
 | Willow_Joystick_Gimbal_Shield.stl | Cover to keep things from falling in the gimbal opening | PLA |  | Any | 1 | 1 | 1 | $25.00 | $0.03 | $0.03
 | Willow_Joystick_Inner_Gimbal_1.stl | One half of inner gimbal | PLA |  | Any | 1 | 2 | 2 | $25.00 | $0.05 | $0.05
 | Willow_Joystick_Inner_Gimbal_2.stl | One half of inner gimbal | PLA |  | Any | 1 | 2 | 2 | $25.00 | $0.05 | $0.05
 | Willow_Joystick_Outer_Gimbal.stl | One half of outer gimbal | PLA |  | Any | 2 | 3 | 6 | $25.00 | $0.15 | $0.15
 | Willow_Joystick_Pin.stl | Pin to hold RJ11 Jack | PLA |  | Any | 1 | 1 | 1 | $25.00 | $0.03 | $0.03
 | Willow_Joystick_Shell.stl | Cover for joystick body | PLA |  | Any | 1 | 18 | 18 | $25.00 | $0.45 | $0.45
 | Willow_Joystick_Sled_1.stl | One half of gimbal sled | PLA |  | Any | 1 | 3 | 3 | $25.00 | $0.08 | $0.08
 | Willow_Joystick_Sled_2.stl | One half of gimbal sled | PLA |  | Any | 1 | 3 | 3 | $25.00 | $0.08 | $0.08
 | Willow_Topper_Concave.stl | Concave topper for joystick | PLA |  | Any | 1 | 2 | 2 | $25.00 | $0.05 | $0.05
 | Willow_Topper_Convex.stl | Convex toper for joystick | PLA |  | Any | 1 | 3 | 3 | $25.00 | $0.08 | $0.08
 | Willow_Topper_Goalpost.stl | Goalpost topper for joystick | PLA |  | Any | 1 | 3 | 3 | $25.00 | $0.08 | $0.08
 | Willow_Topper_Mouldable.stl | Joystick topper that is compatible with mouldable plastic pellets | PLA |  | Any | 1 | 3 | 3 | $25.00 | $0.08 | $0.08
 | Willow_Joystick_Topper_Stick.stl | Stick topper for joystick | PLA |  | Any | 1 | 4 | 4 | $25.00 | $0.10 | $0.10
 | Willow_Hub_Bottom.stl | Bottom of hub enclosure | PLA |  | Any | 1 | 27 | 27 | $25.00 | $0.68 | $0.68
 | Willow_Hub_LED_Spacer.stl | Spacer for hub LEDs | PLA |  | Any | 1 | 3 | 3 | $25.00 | $0.08 | $0.08
 | Willow_Hub_Next_Button.stl | Button for Next input | PLA |  | Any | 1 | 1 | 1 | $25.00 | $0.03 | $0.03
 | Willow_Hub_Select_Button.stl | Button for Select input | PLA |  | Any | 1 | 1 | 1 | $25.00 | $0.03 | $0.03
 | Willow_Hub_Top.stl | Top of hub enclosure | PLA |  | Any | 1 | 18 | 18 | $25.00 | $0.45 | $0.45
 | Willow_Hub_Stand_Front.stl | Main body of hub stand | PLA |  | Any | 1 | 12 | 12 | $25.00 | $0.30 | $0.30
 | Willow_Hub_Stand_Leg.stl | Leg for hub stand | PLA |  | Any | 2 | 4 | 8 | $25.00 | $0.20 | $0.20
 | Willow_Joystick_Wrist_Ramp.stl | Ramp to raise the users wrist | PLA |  | Any | 1 | 4 | 4 | $25.00 | $0.10 | $0.10
 | Willow_Joystick_NonSlip_Foot.stl | Non Slip Foot for the joystick | PLA |  | Any | 1 | 4 | 4 | $25.00 | $0.10 | $0.10
 | Joystick_Camera_Mount_Adaptor.stl | Adaptor for 1/4-20 thread mounting | PLA |  | Any | 1 | 9 | 9 | $25.00 | $0.23 | $0.23
 | Joystick_RAM_B_Mount_Adaptor.stl | Adaptor for RAM arm mounting | PLA |  | Any | 1 | 11 | 11 | $25.00 | $0.28 | $0.28
 | Custom PCB |  |  |  |  |  |  |  |  | $6.00 | $30.00
 | Part | Description |  | Manufacturer | Supplier | QTY / Device | QTY / PKG | PKGs | $/ PKG | $ / Device | Total Estimated Cost |  | Link
 |  | Willow Hub PCB |  |  |  | 1 | 5 | 1 | $5.00 | $1.00 | $5.00
 |  | Shipping |  |  |  | 1 | 5 | 1 | $25.00 | $5.00 | $25.00
 | Tools
 | Tool | Description |  | Manufacturer | Supplier |  |  |  |  |  |  |  | Link
 | Alternatives
 | Part | Description |  | Manufacturer | Supplier | QTY / Device | QTY / PKG | PKGs | $/ PKG | $ / Device | Total Estimated Cost |  | Link

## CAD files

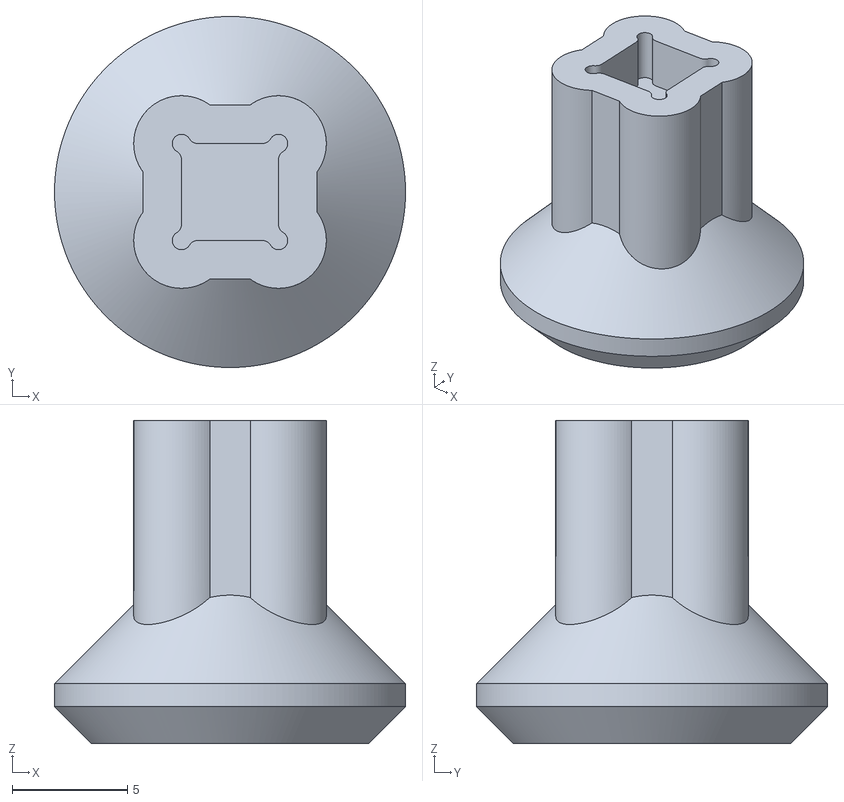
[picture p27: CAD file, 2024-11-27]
Build_Files/3D_Printing_Files/Hub/Willow_Hub_Next_Button.stl
15.2 x 15.2 x 14.0

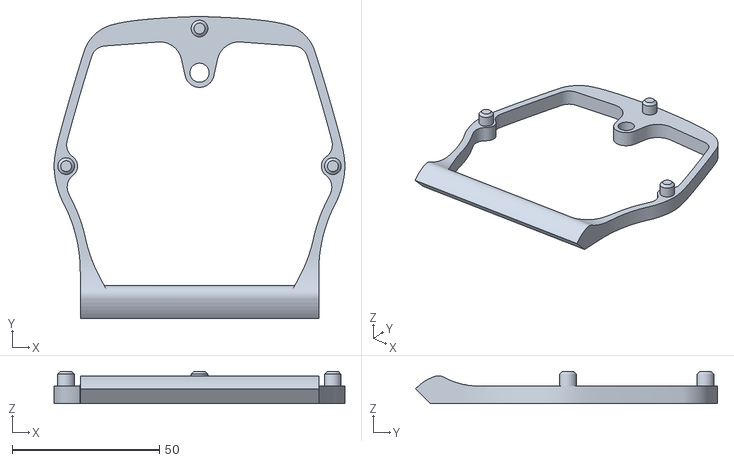
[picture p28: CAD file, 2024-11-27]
Build_Files/3D_Printing_Files/Hub/Willow_Hub_Stand/Willow_Hub_Stand_Front.stl
98.8 x 102.6 x 11.0

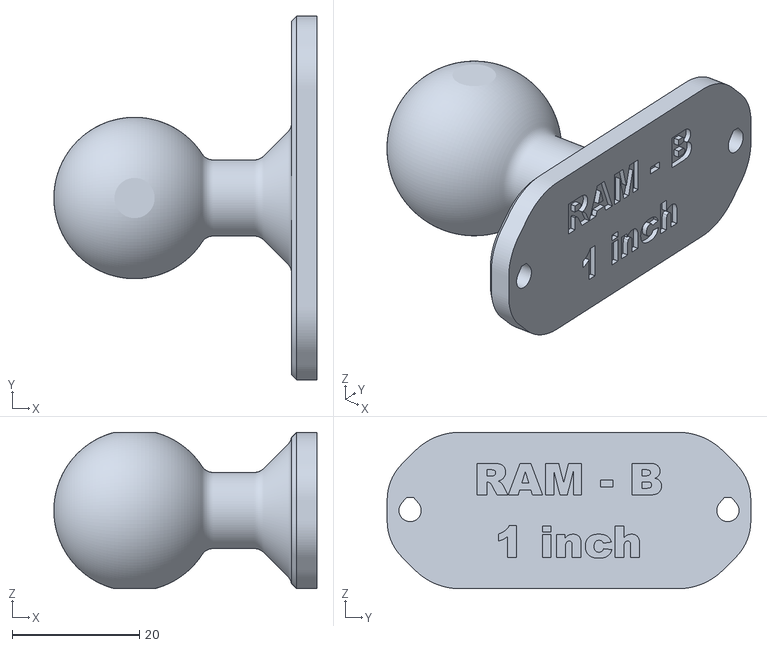
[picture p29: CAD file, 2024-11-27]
Build_Files/3D_Printing_Files/Joystick/Mounting/Joystick_RAM_B_Mount_Adapter.stl
41.4 x 57.2 x 24.6

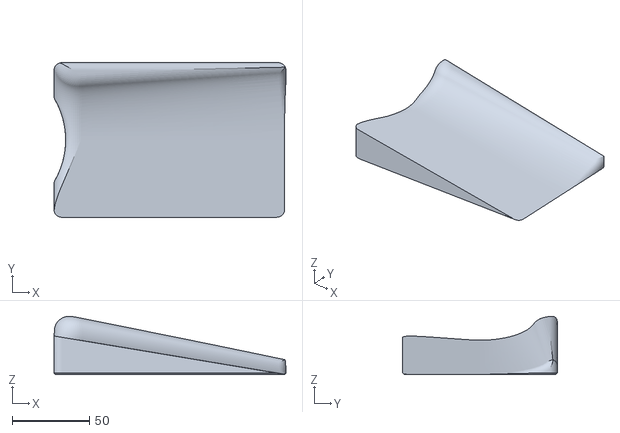
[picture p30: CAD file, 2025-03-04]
Build_Files/3D_Printing_Files/Joystick/Optional/Willow_Joystick_Wrist_Ramp_LeftFlat.stl
150.0 x 100.0 x 37.7

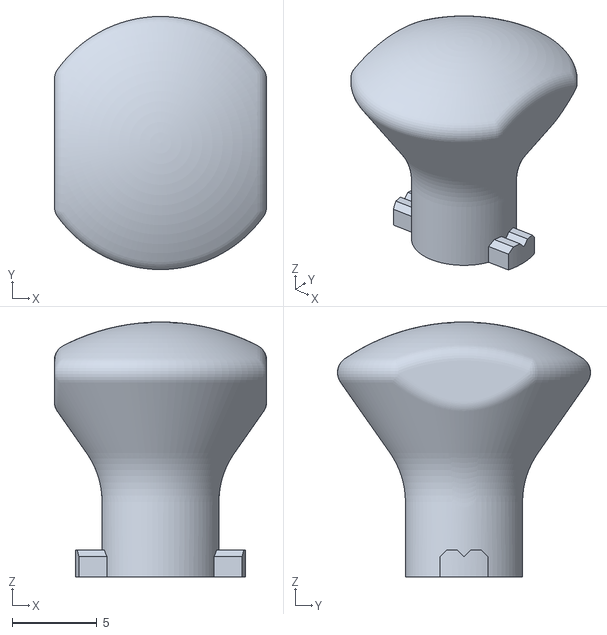
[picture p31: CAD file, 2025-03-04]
Build_Files/3D_Printing_Files/Joystick/Toppers/Willow_Topper_Convex.stl
12.5 x 14.9 x 15.0

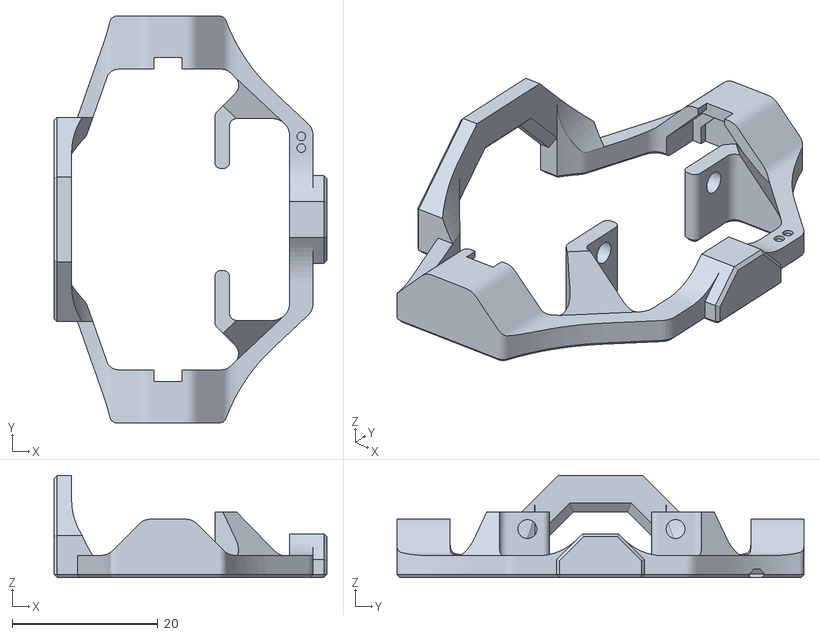
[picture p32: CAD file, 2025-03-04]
Build_Files/3D_Printing_Files/Joystick/Willow_Joystick_Sled_2.stl
37.4 x 55.8 x 14.0

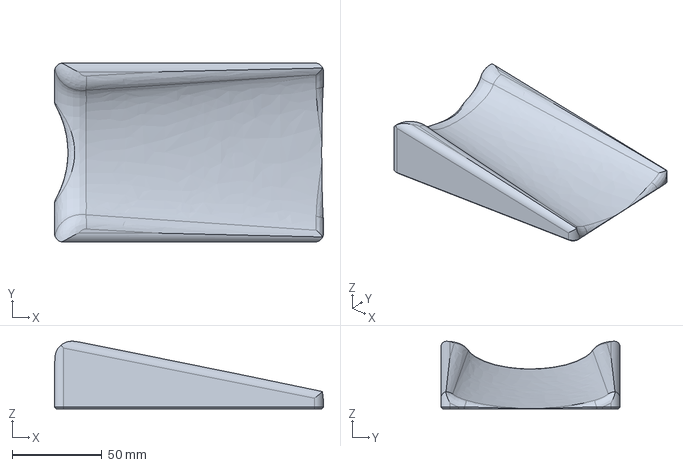
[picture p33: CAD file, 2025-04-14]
Design_Files/CAD_Design_Files/STEP/Optional/Willow Arm Ramp.step
150.0 x 100.0 x 37.7 mm

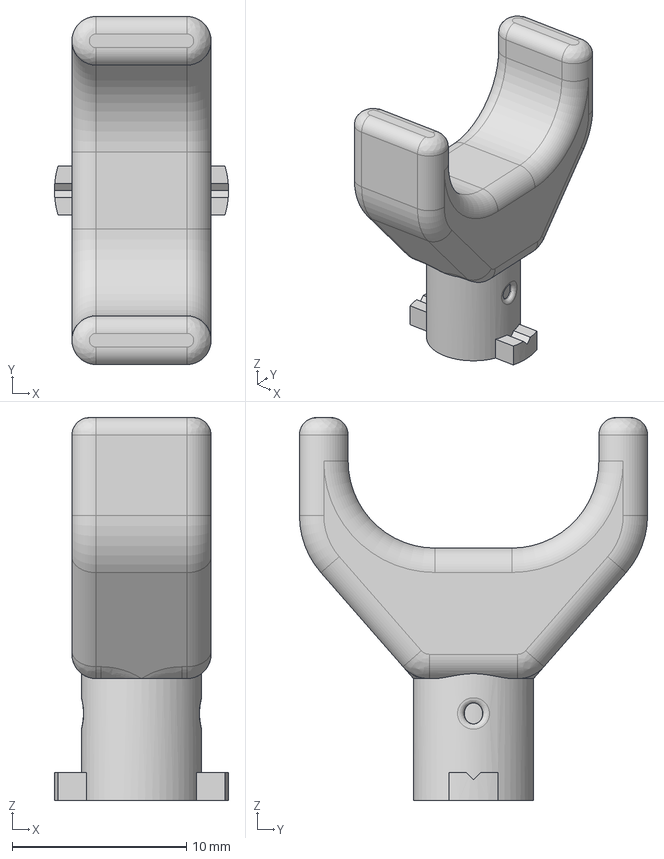
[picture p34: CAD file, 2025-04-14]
Design_Files/CAD_Design_Files/STEP/Toppers/Goalpost Topper Medium.step
10.0 x 20.0 x 22.0 mm

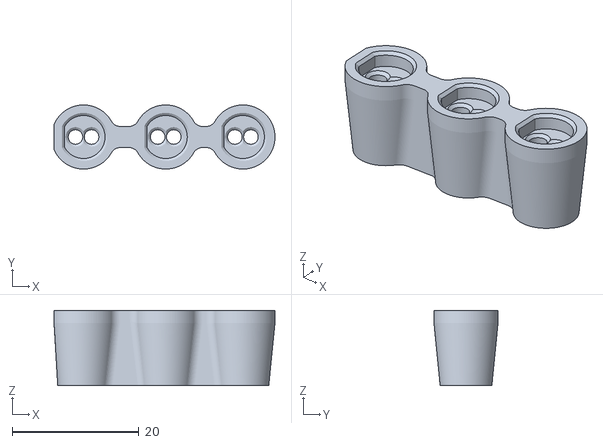
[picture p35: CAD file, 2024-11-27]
Build_Files/3D_Printing_Files/Hub/Willow_Hub_LED_Spacer.stl
34.9 x 10.1 x 11.9

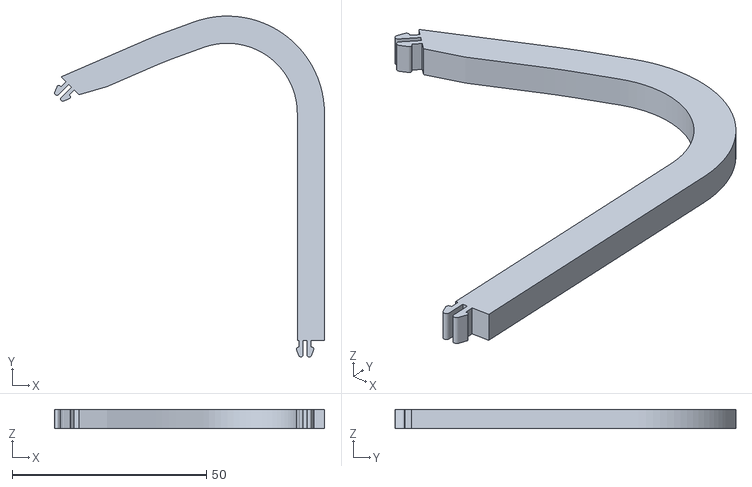
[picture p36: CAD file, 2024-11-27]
Build_Files/3D_Printing_Files/Hub/Willow_Hub_Stand/Willow_Hub_Stand_Leg.stl
69.4 x 87.6 x 5.00

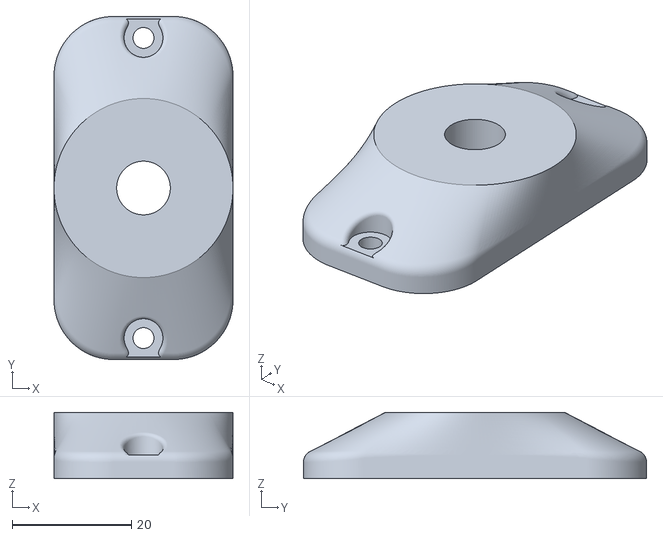
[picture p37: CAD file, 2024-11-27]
Build_Files/3D_Printing_Files/Joystick/Mounting/Joystick_Camera_Mount_Adapter.stl
30.0 x 57.5 x 11.1

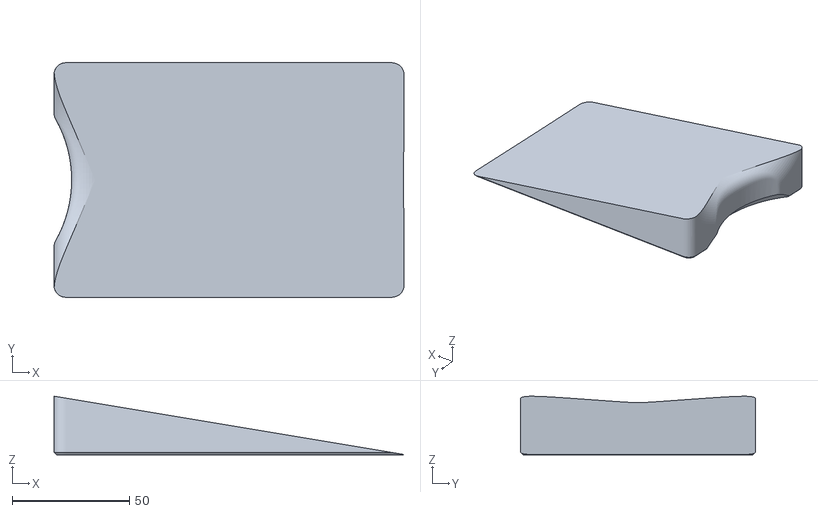
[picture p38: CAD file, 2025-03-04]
Build_Files/3D_Printing_Files/Joystick/Optional/Willow_Joystick_Wrist_Ramp_BothFlat.stl
149.1 x 100.0 x 25.0

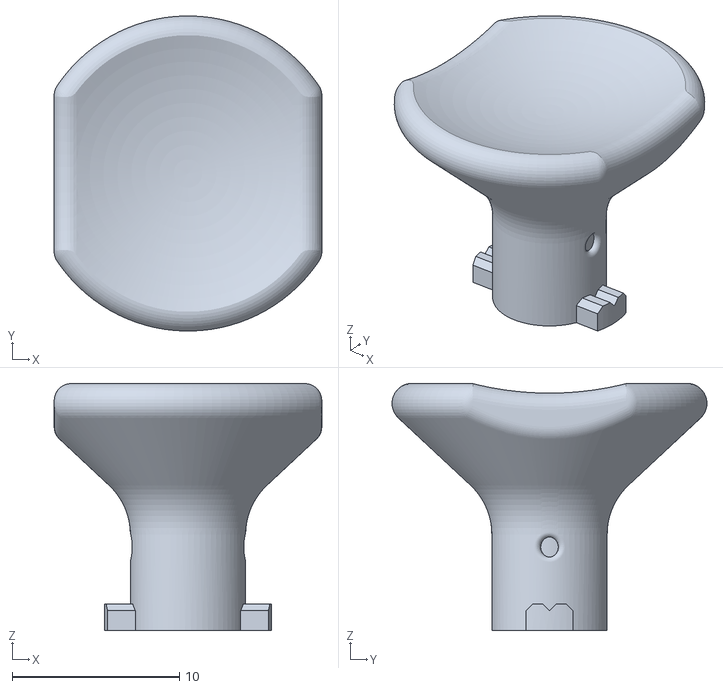
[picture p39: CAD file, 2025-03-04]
Build_Files/3D_Printing_Files/Joystick/Toppers/Willow_Topper_Concave.stl
16.0 x 18.8 x 14.8

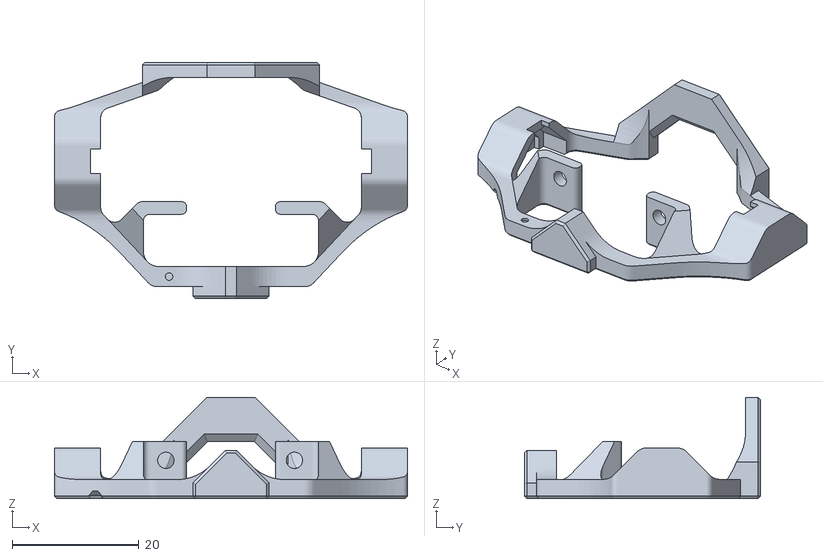
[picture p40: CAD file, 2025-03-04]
Build_Files/3D_Printing_Files/Joystick/Willow_Joystick_Sled_1.stl
55.8 x 37.4 x 16.0

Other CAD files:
Design_Files/CAD_Design_Files/STEP/Toppers/Stick Topper.step
Build_Files/3D_Printing_Files/Hub/Willow_Hub_Bottom.stl
Build_Files/3D_Printing_Files/Joystick/Optional/Willow_Joystick_Wrist_Ramp.stl
Build_Files/3D_Printing_Files/Joystick/Toppers/Willow_Topper_Stick.stl
Build_Files/3D_Printing_Files/Hub/Willow_Hub_Select_Button.stl
Build_Files/3D_Printing_Files/Hub/Willow_Hub_Top.stl
Build_Files/3D_Printing_Files/Joystick/Optional/WIllow_Joystick_NonSlip_Foot.stl
Build_Files/3D_Printing_Files/Joystick/Optional/Willow_Joystick_Wrist_Ramp_RightFlat.stl
Build_Files/3D_Printing_Files/Joystick/Toppers/Willow_Topper_Goalpost_Large.stl
Build_Files/3D_Printing_Files/Joystick/Toppers/Willow_Topper_Goalpost_Medium.stl
Build_Files/3D_Printing_Files/Joystick/Toppers/Willow_Topper_Goalpost_Small.stl
Build_Files/3D_Printing_Files/Joystick/Toppers/Willow_Topper_Mouldable.stl
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

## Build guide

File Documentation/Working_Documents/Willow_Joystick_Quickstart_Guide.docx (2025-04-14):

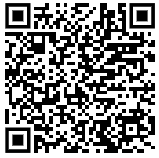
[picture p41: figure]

User Guide (https://github.com/makersmakingchange/Willow-Joystick/blob/main/Documentation/Willow_Joystick_User_Guide.pdf)

# Introduction

The Willow is a magnetic low force joystick that allows a user with limited arm strength to control a computer, gaming console, smart phone, or tablet.

This Quickstart Guide is meant to briefly introduce the functions and use of the Willow. For more detailed information, please consult the User Guide.

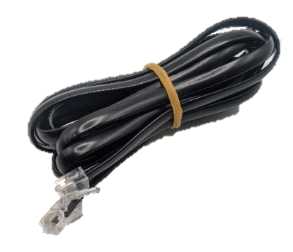
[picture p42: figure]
A picture of the RJ11 cable
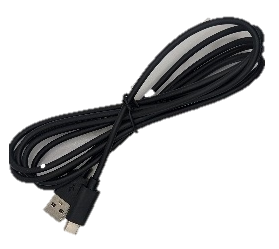
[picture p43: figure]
A photo of a black USB-C cable on a white background.

# Features

Willow Interface Cable

USB-C to USB-A Cable

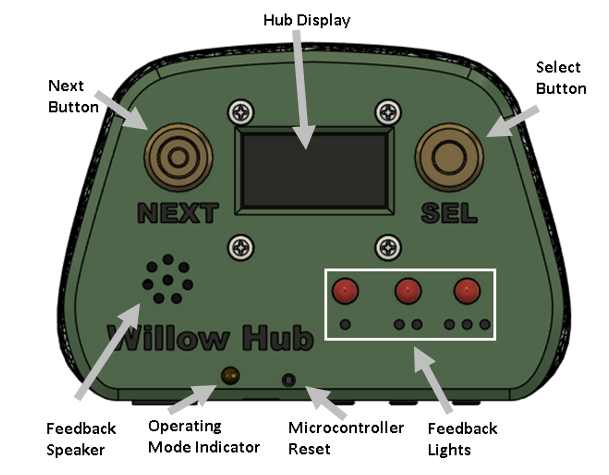
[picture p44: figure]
A diagram of the front of the Willow hub showing the location of buttons, displays, and lights.
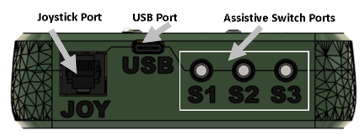
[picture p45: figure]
A diagram of the side of the Willow hub, showing the hub connection points
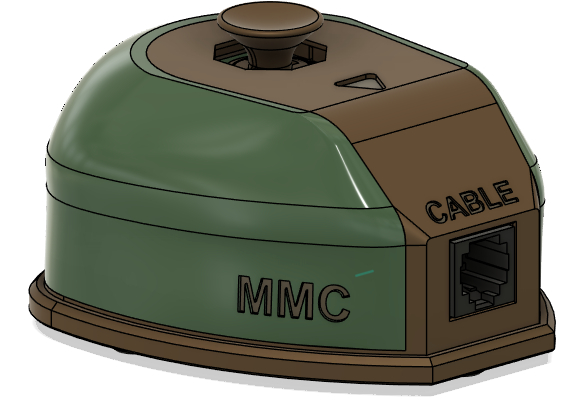
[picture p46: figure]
The willow joystick

Cable Port

Up Direction Marker

Topper

# Setting up the Willow

The following are the general steps needed to setup your Willow Joystick:

1. Mount Willow Joystick a. Mounting adaptors are available 2. Mount Willow Hub a. Hub stand is available 3. Connect Willow Interface Cable | 4. Optional: Connect assistive switches to Willow Hub 5. Connect the Willow Hub to the Host Device 6. Once powered, wait until device initializes before moving joystick.

## USB Connections

For direct USB connection to the host device, connect the appropriate USB cable from the Willow Hub into the host device. Use an adapter if necessary.

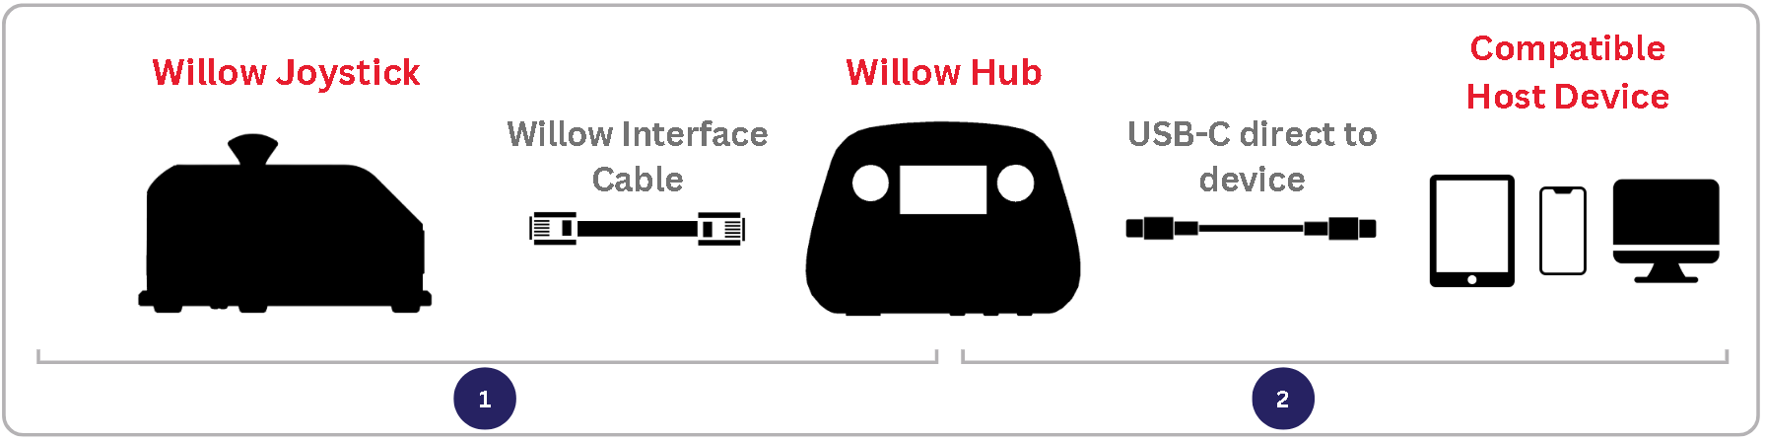
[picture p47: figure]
A generic diagram showing how to connect the Willow to a device

For connection to the host device with an external power source, plug a power splitting adapter into the host device and connect the Willow Hub and external power source to the splitter. Use an Adapter if necessary. Required for iOS USB connection.

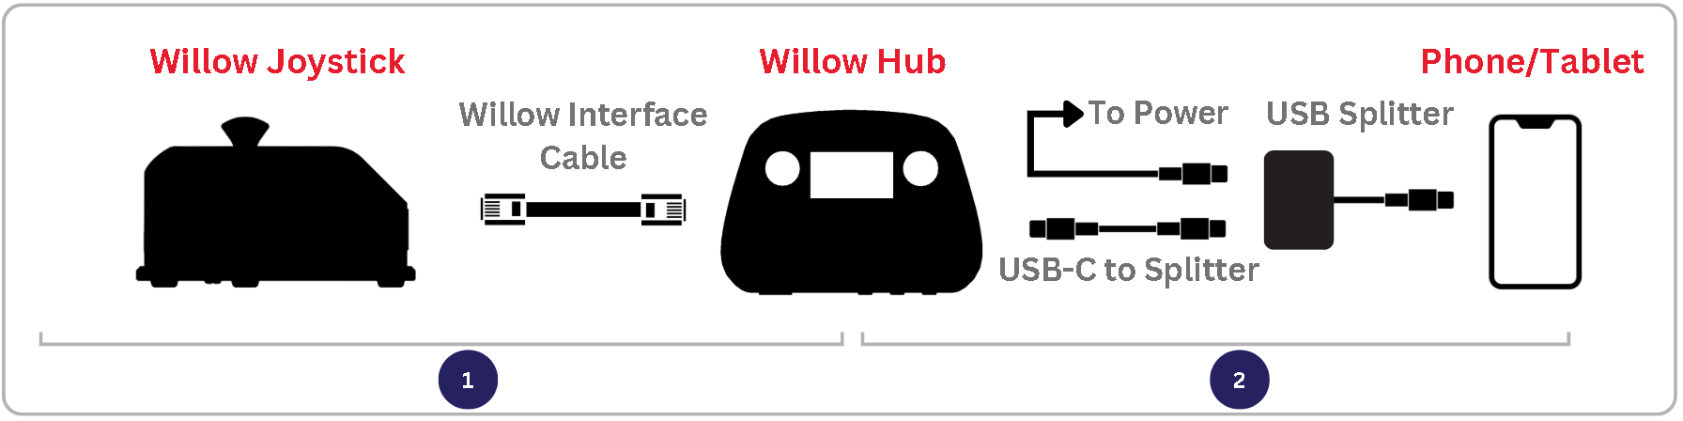
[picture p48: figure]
A diagram showing how to connect the Willow to an iPhone

## Wireless Connections

For wireless connection to the host device, plug the Willow Hub directly into any power source using the appropriate adapter as required. Change the operating mode to BT Mouse through the Hub Menu (See Input Mapping and Settings Menu Options). Find “Willow” in the host device Bluetooth menu to pair and connect.

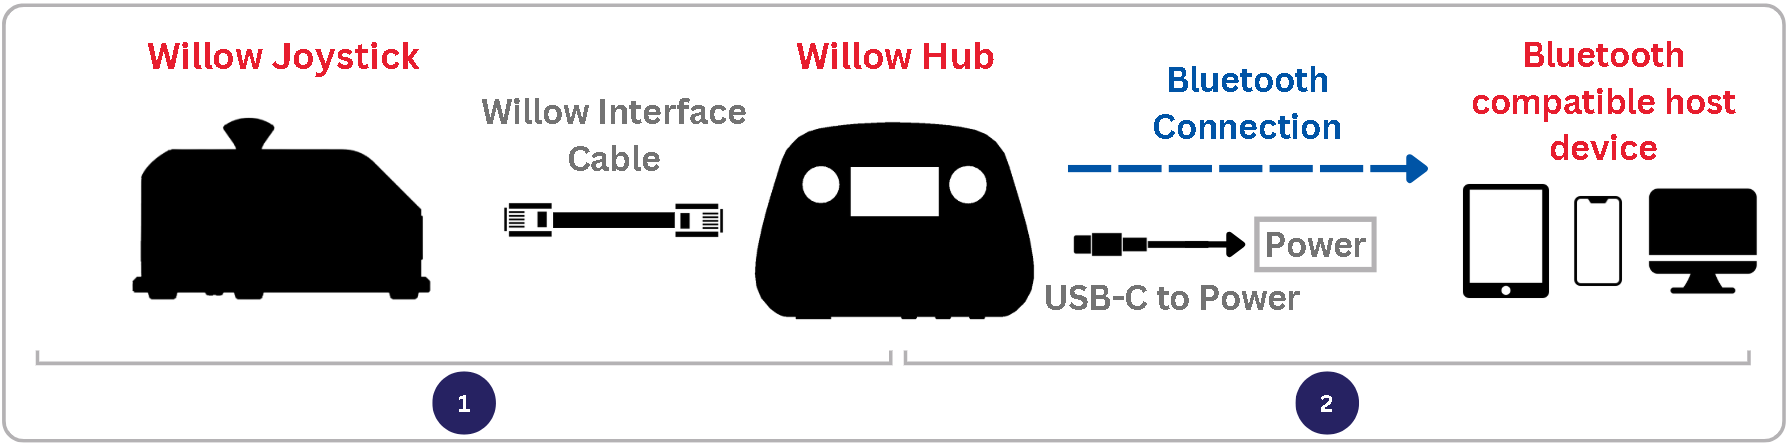
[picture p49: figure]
A diagram showing how to connect the Willow to a Bluetooth device

Cursor Setup on iOS Devices

Open your device’s Settings > Accessibility > Touch > AssistiveTouch > Turn it on.

## Optional: Connecting Assistive Switches

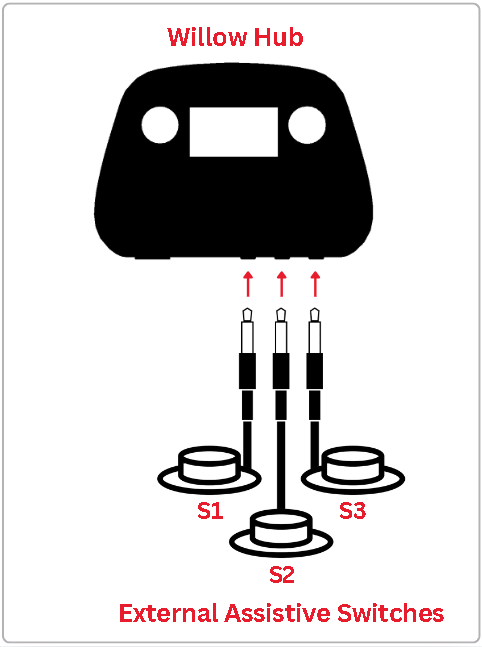
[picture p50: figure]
A diagram of the willow hub showing the hub switch connections

| Up to 3 assistive switches can be connected to the Willow Hub for user inputs. The ports on the Hub for assistive switches are labeled S1, S2, and S3 and are standard 3.5 mm switch ports.

## Input Mapping

Interchangeable Willow Inputs | | Duration | Hub Menu | Mouse | Gamepad
Assistive Switches | Hub Buttons
S1 | Select | < 1 sec | Select | Left click | Button 1
| | 1-3 sec | - | Start Drag Mode | Button 3
| | > 3 sec | Exit Hub Menu | Enter Hub Menu | Enter Hub Menu
S2 | - | < 1 sec | - | Middle Click | Button 5
| | 1-3 sec | - | N/A | Button 6
| | > 3 sec | - | Perform Center Reset | Perform Center Reset
S3 | Next | < 1 sec | Next | Right click | Button 2
| | 1-3 sec | - | Start Scroll Mode | Button 4
| | > 3 sec | - | Middle Click | Button 5
S1 + S3 | Next + Select | < 1 sec | Exit Hub Menu | Enter Hub Menu | Enter Hub Menu
Joystick | | - | - | Cursor movement | Joystick movement

## Hub Menu Settings

The Menu on the Hub Display provides a way to changing operating modes, adjusting settings, activate calibrations, and reset the Willow device. See the Input Action table for how to access and navigate the menu. See the User Guide for more details.

## Troubleshooting

### Cursor Issues

If you are experiencing cursor drift (cursor is moving on device when joystick is not being moved), perform a center reset in one of the following ways:

Option A: Trigger Center Reset Either by: - Navigating through the Hub menu to: Calibrate > Center Reset - Using a very long press of assistive switch 2 | Option B: Turn it off and then on again. Do not touch the joystick until “Ready to use” is displayed on the Hub Display. - Disconnect/Reconnect Willow to power. - Restart the device through the Hub Menu. - Use a paperclip to push the reset pin on the Hub.

### Error Messages

Error Code | Connection Error | | User Action
| Display | Joystick Sensor
ERROR-001 | | ● | 1. Check that the Willow interface cable is securely connected on both ends. 2. Confirm the Willow Interface Cable is the right type. 3. Contact support
ERROR-002 | ● | | 1. Disconnect USB, wait 30 second, reconnect USB. 2. Contact support.
ERROR-003 | ● | ●

## Support

If the issue persists, contact the maker of your device or Makers Making Change at info@makersmakingchange.com

© 2025 by Neil Squire This work is licensed under the CC BY SA 4.0 License: http://creativecommons.org/licenses/by-sa/4.0 Files available at https://github.com/makersmakingchange/Willow-Joystick Page 2 of 3

V1.0| April 2025 Willow Joystick Quickstart Guide

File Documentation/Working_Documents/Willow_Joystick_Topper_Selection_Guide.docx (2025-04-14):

# What is a topper?

A topper is any support, grip, or other structure added to the joystick to make it easier and more comfortable to use the joystick. This is the main part that the user interacts with. Toppers can be made of a variety of materials and be customized to the user.

The Willow Joystick has a modular topper that can be easily swapped. It comes with five different topper options, as well as the design files to create your own custom topper.

The willow joystick

Up Direction Marker

Topper

Joystick

# What styles of toppers are there?

There are currently five different styles of toppers for the Willow: a goalpost topper, a concave topper, a convex topper, a stick topper, and a mouldable plastic topper.

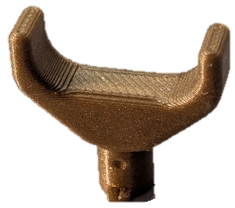
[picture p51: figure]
A photo of the goalpost topper printed in gold
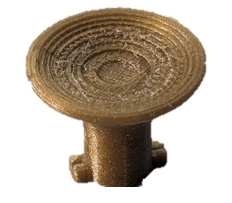
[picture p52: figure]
A photo of the concave topper printed in gold
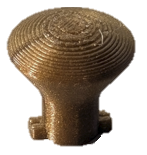
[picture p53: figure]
A photo of the convex topper printed in gold
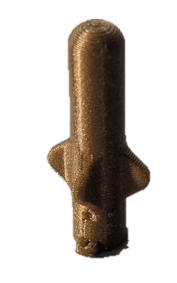
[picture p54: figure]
A photo of the stick topper printed in gold
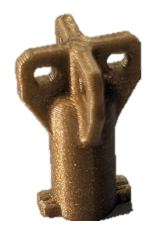
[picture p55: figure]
A photo of the mouldable plastictopper printed in gold

Goalpost | Concave | Convex | Stick | Mouldable Plastic

# What topper will be best for me?

## Goalpost Topper

The Goalpost Topper has a flat bar at the top, with side walls on either side. These walls keep the user’s finger aligned with the up/down direction of the joystick and stop it from sliding off the sides.

There are three different sizes of goalpost topper, with different widths between the two posts. The small topper has a distance of 12mm, the medium topper has a distance of 15mm, and the large topper has a distance of 20mm. For all three toppers, the distance between the top of the joystick and the surface that the users finger rests on is 7.5mm.

## Concave Topper

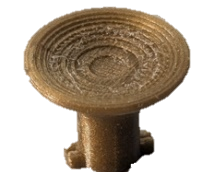
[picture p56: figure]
A photo of the concave topper printed in gold

The Concave Topper has a small cup-like indent at the top, ideal for a user’s finger to rest in and move freely in any direction. The diameter of the cup is 16mm, and the distance between the top of the joystick and the surface that the users finger rests on is 5mm.

## Convex Topper

The Convex Topper has a domed top that rises up, instead of dipping down like the concave topper. It is ideal for use with two fingers, or with one finger if retainment/alignment is not a concern. The topper has a diameter of 15mm and the top of the dome sits 7.5mm above the top of the joystick.

## Stick Topper

The Stick Topper is a tube with a rounded top. It has four fins at the base to allow the secondary user to grip it and more easily apply force to turn the gutter lock. It aims to mimic the topper found on the joystick mechanisms used in devices such as the Oak Joystick (https://www.makersmakingchange.com/s/product/oak-compact-joystick/01tJR00000092x3YAA). The diameter of the stick is 7mm and the distance from the top of the stick to the top of the joystick is 22.5mm.

## Mouldable Plastic Topper

The Mouldable Plastic Topper is designed for use with mouldable plastic pellets to create a custom shaped topper. The fins on the topper provide a surface for the plastic to grip onto once it has cooled and been shaped into the ideal topper. The width of the 3D printed fins is 12.5mm and the distance from the top of the fins to the top of the joystick is 12.5mm, but the final dimensions depend on the shape of the heat moulded plastic.

When adding plastic pellets, try to use the minimum amount possible to avoid adding weight to the topper. Adding too much may cause the joystick to have difficulty centering. Making the topper taller will also cause issues centering.

## Custom Topper

If none of the existing topper options are suitable for the user’s needs, the Fusion 360 file to make a custom topper is included in the design files, named Template Topper.f3d. The custom topper file has the correctly sized tabs and stem to interface with the gimbal in the joystick. There is a dot on two sides of the topper to indicate the up/down direction of the joystick when locked into the gimbal. This dot can be used to orient the topper when designing a custom topper that needs to be in a certain direction when installed, such as the goalpost topper. There are two dots instead of one since the topper can be inserted into the gimbal in one of two orientations, so either dot could be the one facing the up direction of the joystick.

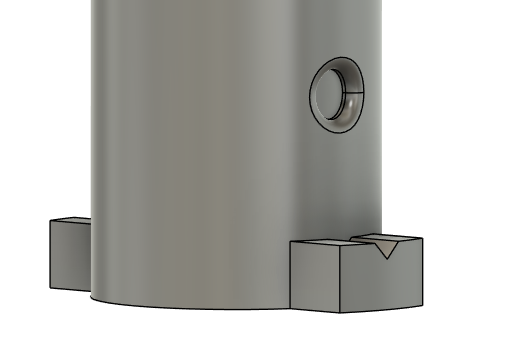
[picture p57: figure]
An image of the CAD of the generic topper connection system

When designing a topper, make sure to include a feature that allows the user to apply enough force when twisting to fully lock the topper in place. The stick topper has the four ‘fins’ because just having the stick itself did not allow the user to lock the topper in place.

# Topper Sizing Printout

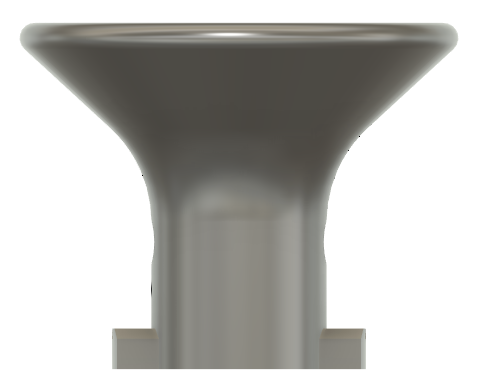
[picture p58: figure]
A scale image of the concave topper
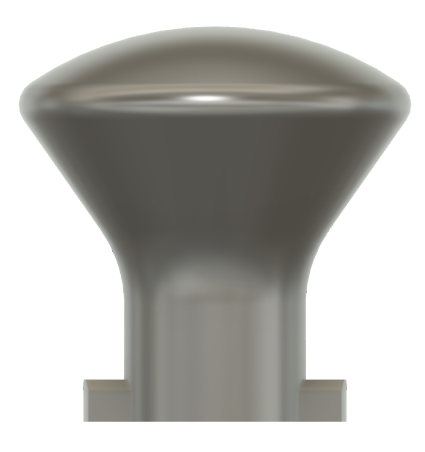
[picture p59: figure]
A scale image of the convex topper
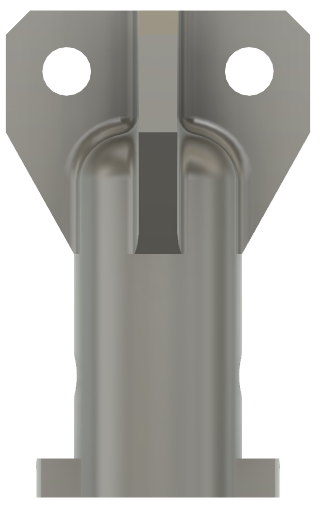
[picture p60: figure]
A scale image of the mouldable topper

Concave Topper | Convex Topper | Mouldable Topper

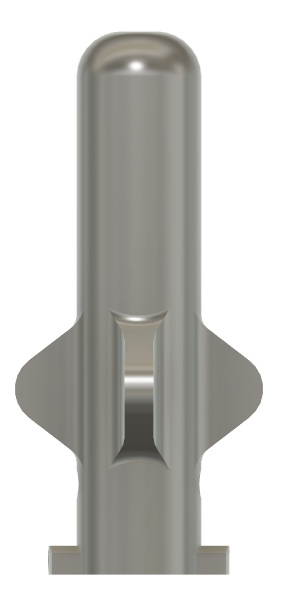
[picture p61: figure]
A scale image of the stick topper
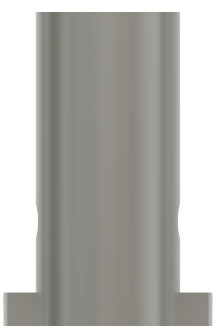
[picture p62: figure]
A scale image of the template topper

Stick Topper | Template Topper

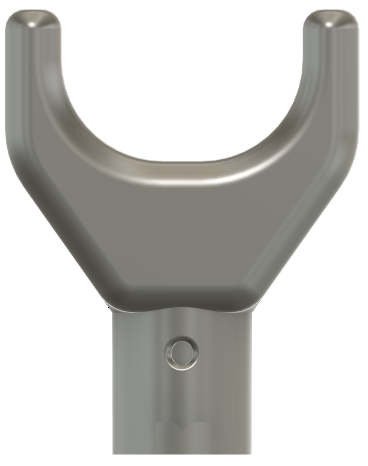
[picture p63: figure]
A scale image of the small goalpost topper
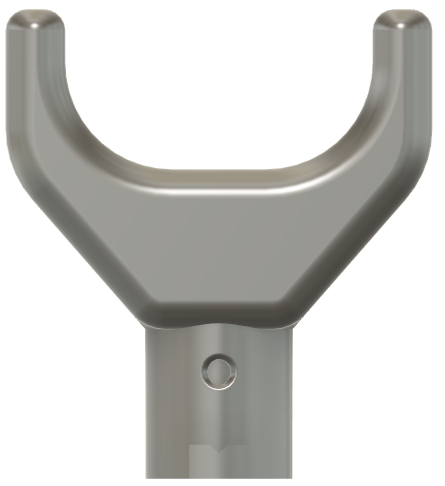
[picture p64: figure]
A scale image of the medium goalpost topper
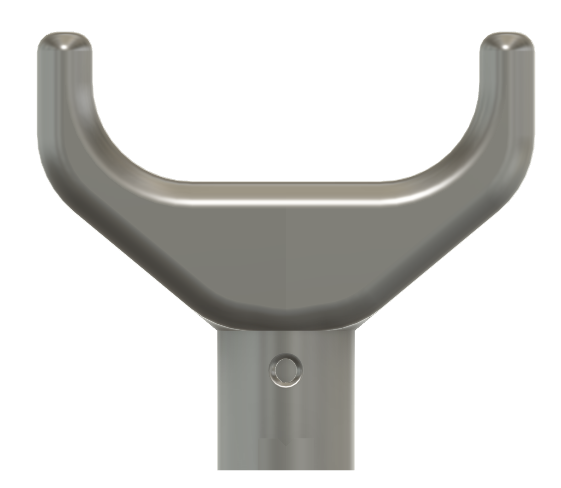
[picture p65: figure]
A scale image of the large goalpost topper

Small Goalpost Topper | Medium Goalpost Topper | Large Goalpost Topper

© 2025 by Neil Squire. This work is licensed under the CC BY SA 4.0 License: http://creativecommons.org/licenses/by-sa/4.0 Files available at https://github.com/makersmakingchange/Willow-Joystick Page 48 of 50

V1.0 | APRIL 2025 Willow Joystick Topper Selection guide

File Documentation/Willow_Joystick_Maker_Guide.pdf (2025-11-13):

V1.0.0 | March 2025

## Willow Joystick

## MAKER GUIDE

© 2025 by Neil Squire. (https://neilsquire.ca/)
This work is licensed under the CC BY SA 4.0 License: http://creativecommons.org/licenses/by-sa/4.0 Files available at https://github.com/makersmakingchange/Willow-Joystick Page 1 of 58

### Overview

This document contains the necessary information to build the Willow Joystick, a low force magnetic joystick for users with low strength and range of motion

## MAKER GUIDE

Files available at https://github.com/makersmakingchange/Willow-Joystick Page 2 of 58

### Contents

Overview | 1
Maker Checklist | 4
Maker To Do List | 4
Items to Give to User | 4
Tool List | 5
Tools / Equipment | 5
Supplies | 5
Personal Protective Equipment (PPE) | 5
Customization Guide | 6
Colours | 6
Toppers | 6
Mounting | 6
Custom Printed Circuit Board (PCB) Guide | 7
Ordering the Custom PCB | 7
3D Printing Guide | 8
3D Printing Summary | 8
3D Printing Settings | 8
Post-Processing | 9
Examples of Quality Prints | 10
Maker Component List | 14
Assembly Guide | 20
Part A: Hub PCB Assembly | 21
Part A: Components | 21
Part A: Tools | 22
Part A: Personal Protective Equipment (PPE) | 22
Part A: Hub PCB Assembly Steps | 23
Part B: Hub Enclosure Assembly | 30
Part B: Components | 30
Part B: Tools | 31

## MAKER GUIDE

Files available at https://github.com/makersmakingchange/Willow-Joystick Page 3 of 58

Part B: Personal Protective Equipment (PPE) | 31
Part B: Assembling Hub Enclosure Steps | 32
Part C: Joystick Prep | 37
Part C: Required Components | 37
Part C: Required Tools and Supplies | 37
Part C: Required Personal Protective Equipment (PPE)Safety glasses | 37
Part C: Joystick Assembly Steps | 37
Part D: Flashing Firmware to Willow | 40
Part D: Required Components | 40
Part D: Required Tools and Supplies | 40
Part E: Joystick Assembly | 42
Part E: Required Components | 42
Part E: Required Tools and Supplies | 43
Part E: Joystick Assembly Steps | 44
Part F: Optional Components | 52
Part F: Required Components | 52
Part F: Required Tools and Supplies | 52
Testing | 56
Testing the Willow | 56
Testing Mouse Mode | 56
Testing External Switches | 56
Testing Hub Buttons | 56
Troubleshooting | 57

## MAKER GUIDE

Files available at https://github.com/makersmakingchange/Willow-Joystick Page 4 of 58

### Maker Checklist

This list provides an overview of the steps required to build and deliver the Willow Joystick.

### Maker To Do List

Read through the Maker Guide to become familiar with required components, tools, supplies, safety gear, and overall assembly steps.
Talk to the User about customization options
- Refer to the Customization Guide section of the Maker Guide
- Colour of hub, colour of joystick
- Joystick shell and base can be separate colours for a two-tone effect.
- What toppers do they want
- Review the topper selection guide for what toppers are available
- What mounting supplies do they need
- Camera mount adaptors, non-slip feet, hub stand, mounting arms, etc.
- Do they want a wrist ramp
- Flat ramp, right side flat, left side flat, no sides flat
- Do they want the standard size, or a customized one.
- How they would like to receive the “User Guide” (PDF or physical copy) Order custom PCB
Order hardware components
Gather tools, supplies, and safety equipment.
Assemble the Willow Hub
Assemble the Willow Joystick
Flash firmware to the Willow Hub
Test the Willow Joystick
Print “Quickstart Guide” (if the User would like a physical copy)

### Items to Give to User

Willow Joystick
Joystick Toppers
Willow Hub
USB C cable
RJ11 Cable
Hub Stand (If asked for)
Non- Slip Foot (If asked for)
Camera Mount Adaptor (If asked for) “User Guide”
“Quick Start Guide”

## MAKER GUIDE

Files available at https://github.com/makersmakingchange/Willow-Joystick Page 5 of 58

### Tool List

### Tools / Equipment

Tool
ID
Description | Required / Recommended

Notes

T01 | Soldering Iron | Required | For soldering electronic components.
T02 | Wire Strippers | Recommended | For stripping the insulation off the stemma-Dupont cable if the headers fall off
T03 | Phillips Screwdriver | Required | A jeweller’s screwdriver or similar for securing M2.5 machine screws
T04 | Flush Cutters | Required | For trimming soldered leads
T05 | Crescent wrench / wrench / hex key | Recommended | For installing T-nuts into Hub and Joystick enclosures.
T06 | Sandpaper/Files | Recommended | Cleaning up 3d prints; fixing bearing fits
T07 | Needle Nose Pliers | Recommended | Installing bearings; routing cables
T08 | Computer with Arduino IDE | Required | For flashing firmware to microcontroller

### Supplies

Supplies ID Description | Quantity | Notes
S01 | Solder | <6 inches | Soldering

### Personal Protective Equipment (PPE)

PPE ID | Description | Notes
P01 | Safety Glasses | Preventing things from flying into the maker’s
eye when trimming wires or other parts.

## MAKER GUIDE

Files available at https://github.com/makersmakingchange/Willow-Joystick Page 6 of 58

### Customization Guide

### Colours

- The joystick and hub can be printed in the user’s desired colour.
- The text on the joystick and hub can be printed in a different colour using a printer with a multi material system, or a colour swap can be done on the hub after the first two layers to increase the contrast on the hub. A second layer swap can also be used to make the hub colours more consistent.

### Toppers

- There are a variety of toppers available, as well as the base file to design your own custom topper. Refer to the included topper selection guide for more information. Make sure to consult with the user on this so that they can pick the best topper for them.
- If the user does not like any of the toppers available, there is a Fusion 360 file available to create a custom topper, as well as a topper intended for use with heat moldable plastic pellets

### Mounting

- There is an optional arm rest available, with the design file included if the user needs a different height, length, etc.
- There is an optional non-slip base available for the Joystick, as well as mounting adaptors for ¼-20 thread and RAM B mount.
- There is an optional but recommended hub stand to keep the hub at a visible angle for the user.

## MAKER GUIDE

Files available at https://github.com/makersmakingchange/Willow-Joystick Page 7 of 58

### Custom Printed Circuit Board (PCB) Guide

The Willow Joystick Hub uses one custom circuit board. This circuit board is the same one used in the LipSync Hub.

The Custom PCB can be ordered from one of a variety of PCB Manufacturers. Typically, the minimum quantity for a custom PCB is five. Shipping options vary significantly in cost and shipping time. Plan on at least a week from the time of order to the PCBs arrival.

### Ordering the Custom PCB

1. Select a PCB Fabrication Company
a. JLPCB (https://jlcpcb.com/)
b. PCBWay (https://www.pcbway.com/)
c. OSH Park (https://oshpark.com/)
d. Seeed Fusion PCB (https://www.seeedstudio.com/fusion_pcb.html)
2. Create an account or use a guest login.
3. Upload the Gerber Files (e.g., LipSync_Hub_PCB_2024-02-09.zip).
4. Select the fabrication options:
a. PCB Layers: 2 Layers
b. PCB Quantity: 1 (Some companies have a minimum PCB order more than this, usually 5)
c. PCB Thickness: 1.5 mm
d. Surface Finish: HASL
e. PCB Color: Choose what you like. Note that certain colours may impact build time and cost.
f. The default settings for the other settings should work.
5. Select shipping option.
a. Shipping options and costs vary significantly. Select the best option based on your budget and timing.
6. Submit the order.

## MAKER GUIDE

Files available at https://github.com/makersmakingchange/Willow-Joystick Page 8 of 58

### 3D Printing Guide

The device was originally printed on a Bambu P1S using Bambu Studio

The default speeds were used on all parts except for the two sled pieces. For these prints all speeds and accelerations were turned to 50% of the default value.

### Testing has shown that a printer with automatic bed leveling is needed to

properly print the components in the gimbal.

### 3D Printing Summary

Metrics | Total | Hub | Joystick | Optional
Total Print Time (hour min) | 8:11 | 1:54 | 2:19 | 3:58
Total Number of Components | 27 | 5 | 10 | 12
Typical Total Mass (g) | 243 | 49 | 56 | 138
Typical Number of Print Setups | 4 | 1 | 2 | 1

### 3D Printing Settings

Note that the 3D printing material should be assumed to be PLA unless otherwise noted in the table below.

Print File Name | Qty | Total Print Time (hr:min)

Mass
(g)

Infill
(%)

Support
(Y/N)

Layer
Height/
Nozzle
Diameter
(mm)

Notes

Hub Files

Willow_Hub_Bottom.stl | 1 | 1:00 | 27 | 20 | N | 0.2/0.4
Willow_Hub_LED_Spacer.stl | 1 | 0:07 | 2 | 20 | N | 0.2/0.4
Willow_Hub_Next_Button.stl | 1 | 0:05 | 1 | 20 | N | 0.2/0.4
Willow_Hub_Select_Button.stl | 1 | 0:05 | 1 | 20 | N | 0.2/0.4
Willow_Hub_Top.stl | 1 | 0:37 | 18 | 20 | N | 0.2/0.4

Joystick Files

Willow_Joystick_Base.stl | 1 | 0:52 | 22 | 20 | N | 0.2/0.4
Willow_Joystick_Shell.stl | 1 | 0:31 | 17 | 20 | N | 0.2/0.4
Willow_Joystick_Inner_Gimbal_1.stl | 1 | 0:07 | 2 | 20 | N | 0.2/0.4
Willow_Joystick_Inner_Gimbal_2.stl | 1 | 0:07 | 2 | 20 | N | 0.2/0.4
Willow_Joystick_Outer_Gimbal.stl | 2 | 0:08 | 3 | 20 | N | 0.2/0.4

## MAKER GUIDE

Files available at https://github.com/makersmakingchange/Willow-Joystick Page 9 of 58

Willow_Joystick_Sled_1.stl | 1 | 0:11 | 3 | 20 | N | 0.2/0.4 | Print at half speed
Willow_Joystick_Sled_2.stl | 1 | 0:11 | 3 | 20 | N | 0.2/0.4 | Print at half speed
Willow_Joystick_Gimbal_Shield.stl | 1 | 0:03 | 1 | 20 | N | 0.2/0.4
Willow_Joystick_Pin.stl | 1 | 0:01 | 1 | 20 | N | 0.2/0.4

Joystick Topper Files

Willow_Topper_Concave.stl | 1 | 0:06 | 1 | 20 | N | 0.2/0.4 | Optional
Willow_Topper_Convex.stl | 1 | 0:07 | 1 | 20 | N | 0.2/0.4
Willow_Topper_Goalpost.stl | 1 | 0:09 | 2 | 20 | N | 0.2/0.4 | Optional
Willow_Topper_Stick.stl | 1 | 0:09 | 1 | 20 | N | 0.2/0.4 | Optional
Willow_Topper_Mouldable.stl | 1 | 0:07 | 1 | 20 | N | 0.2/0.4 | Optional

Optional Files

Willow_Joystick_NonSlip_Base.stl | 1 | 0:17 | 13 | 20 | N | 0.2/0.4 | Optional
Joystick_Camera_Mount_Adaptor.stl | 1 | 0:12 | 7 | 20 | N | 0.2/0.4 | Optional
Joystick_RAM_B_Mount_Adapter.stl | 1 | 0:17 | 9 | 20 | N | 0.2/0.4 | Optional
Willow_Joystick_Wrist_Ramp.stl | 1 | 2:00 | 85 | 20 | N | 0.2/0.4 | Optional
Willow_Hub_Stand_Front.stl | 1 | 0:20 | 10 | 20 | N | 0.2/0.4 | Optional
Willow_Hub_Stand_Leg.stl | 2 | 0:07 | 4 | 20 | N | 0.2/0.4 | Optional

### Post-Processing

Inspect the 3D printed parts for any printing defects, sharp edges, or burrs. Sharp edges and burrs can be removed with sanding or deburring tools.

Some parts, such as the concave topper or the wrist ramp, may need a slight sanding to smooth the surface and make them comfortable for the user.

## MAKER GUIDE

Files available at https://github.com/makersmakingchange/Willow-Joystick Page 10 of 58

### Examples of Quality Prints

Compare your 3D prints to the images here. If there are significant differences, you may need to reprint

the part.

Hub Enclosure Assembly

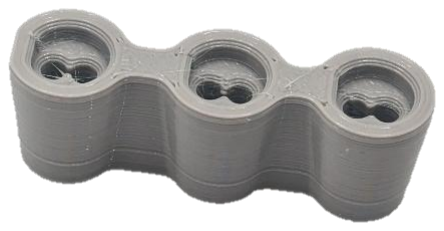
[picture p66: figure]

Willow_Hub_Bottom.stl | Willow_Hub_LED_Spacer.stl | Willow_Hub_Next_Button.s tl
Willow_Hub_Select_Button.stl | Willow_Hub_Top.stl

## MAKER GUIDE

Files available at https://github.com/makersmakingchange/Willow-Joystick Page 11 of 58

Joystick Enclosure Assembly

Willow_Joystick_Base.stl | Willow_Joystick_Gimbal_Shiel d.stl

Willow_Joystick_Inner_Gimbal_ 1.stl

Willow_Joystick_Inner_Gimbal_ 2.stl

Willow_Joystick_Outer_Gimbal .stl

Willow_Joystick_Pin.stl

Willow_Joystick_Shell.stl | Willow_Joystick_Sled_1.stl | Willow_Joystick_Sled_2.stl

## MAKER GUIDE

Files available at https://github.com/makersmakingchange/Willow-Joystick Page 12 of 58

Toppers

Willow_Topper_Concave.stl | Willow_Topper_Convex.stl | Willow_Topper_Goalpost.stl
Willow_Topper_Mouldable.stl | Willow_Topper_Stick.stl

## MAKER GUIDE

Files available at https://github.com/makersmakingchange/Willow-Joystick Page 13 of 58

Optional Parts

Willow_Hub_Stand_Front.stl | Willow_Hub_Stand_Leg.stl | Joystick_Camera_Mount_Adapte r.stl

Joystick_RAM_B_Mount_Adapte r.stl

Willow_Joystick_NonSlip_Bas e.stl

Willow_Joystick_Wrist_Ramp.stl

## MAKER GUIDE

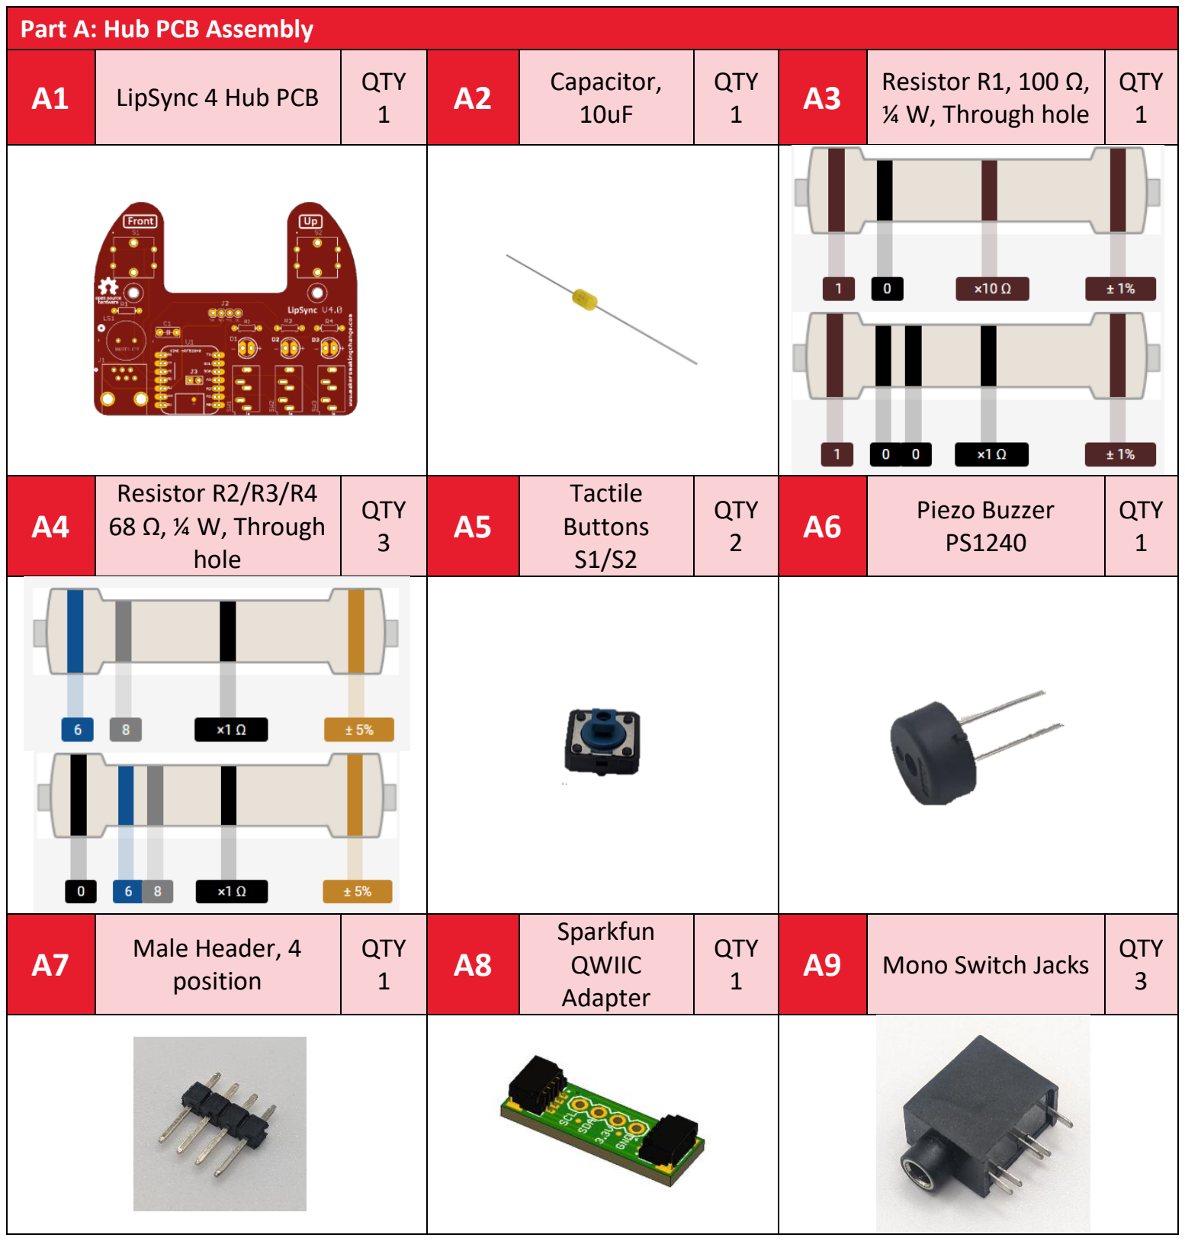
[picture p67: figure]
Part A: Hub PCB Assembly; LipSync 4 Hub PCB; QTY; Capacitor, 10uF; QTY 1; Resistor R1, 100 Ω,; ¼ W, Through hole; Resistor R2/R3/R4 68 Ω, ¼ W, Through hole; QTY 3; Tactile Buttons S1/S2; QTY 2; Piezo Buzzer PS1240; Male Header, 4; position; Sparkfun QWIIC Adapter; Mono Switch Jacks

Files available at https://github.com/makersmakingchange/Willow-Joystick Page 14 of 58

### Maker Component List

## MAKER GUIDE

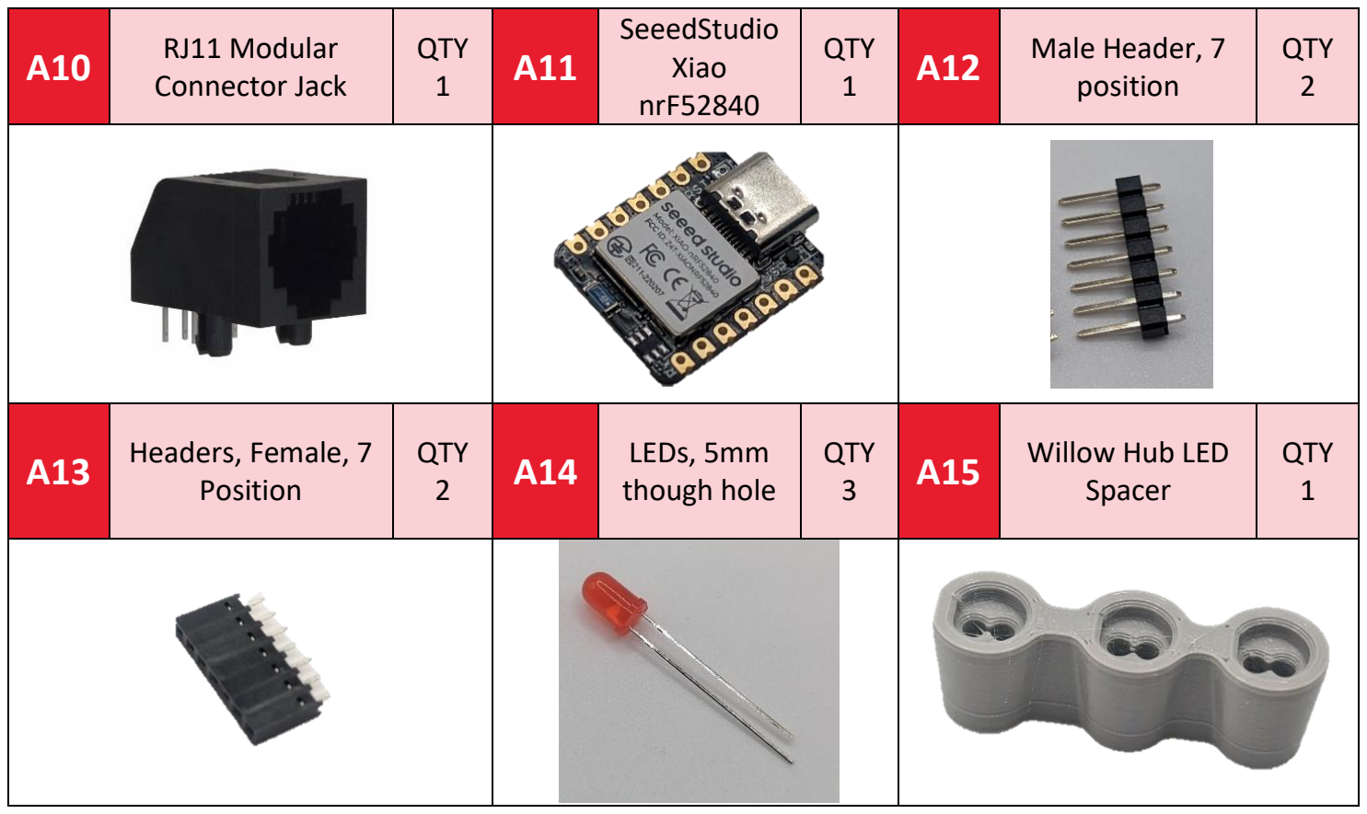
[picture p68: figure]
RJ11 Modular; Connector Jack; QTY 1; SeeedStudio Xiao nrF52840; Male Header, 7; position; QTY 2; Headers, Female, 7; Position; LEDs, 5mm; though hole; QTY 3; Willow Hub LED; Spacer
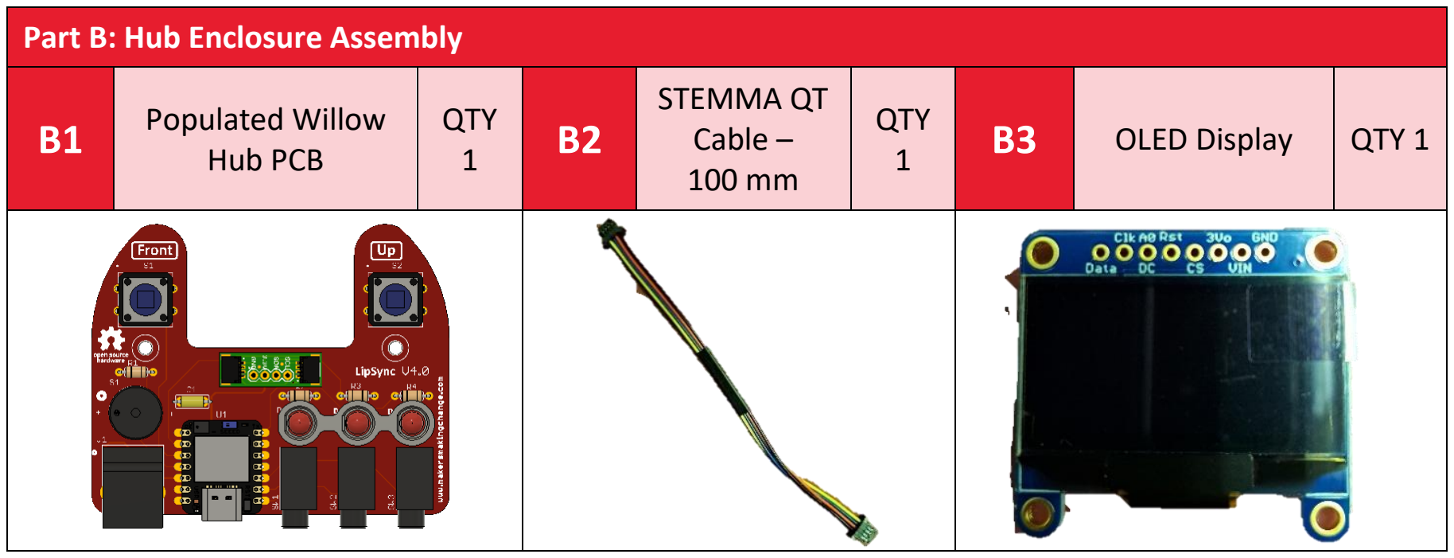
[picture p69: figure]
Part B: Hub Enclosure Assembly; Populated Willow; Hub PCB; QTY 1; STEMMA QT Cable – 100 mm; OLED Display

Files available at https://github.com/makersmakingchange/Willow-Joystick Page 15 of 58

## MAKER GUIDE

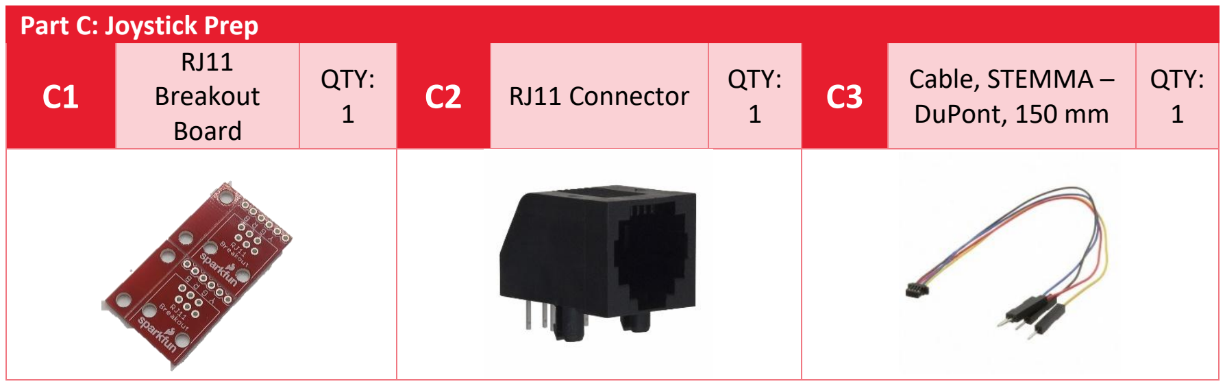
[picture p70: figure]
Part C: Joystick Prep; RJ11 Breakout Board; QTY: 1; RJ11 Connector; QTY:; Cable, STEMMA –; DuPont, 150 mm

Files available at https://github.com/makersmakingchange/Willow-Joystick Page 16 of 58

B4 | Willow Hub
Enclosure Top

QTY
1

B5

Willow Next
Button
Pusher

QTY
1
B6 | Willow Select
Button Pusher | QTY 1
B7 | Willow Hub
Enclosure Bottom

QTY
1

B8 Screw, #4,
3/8” Length

QTY
5

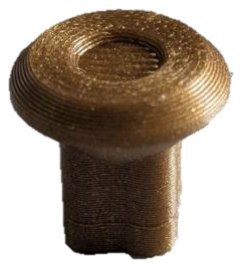
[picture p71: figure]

B9 | M2.5 Machine
Screw, 8 mm | QTY 4
B10 | M2.5 Nut | QTY
4
B12 | T-Nut | QTY
1
B13 | Light Pipe | QTY
1

## MAKER GUIDE

TLV493D STEMMA QT Board; QTY: 1
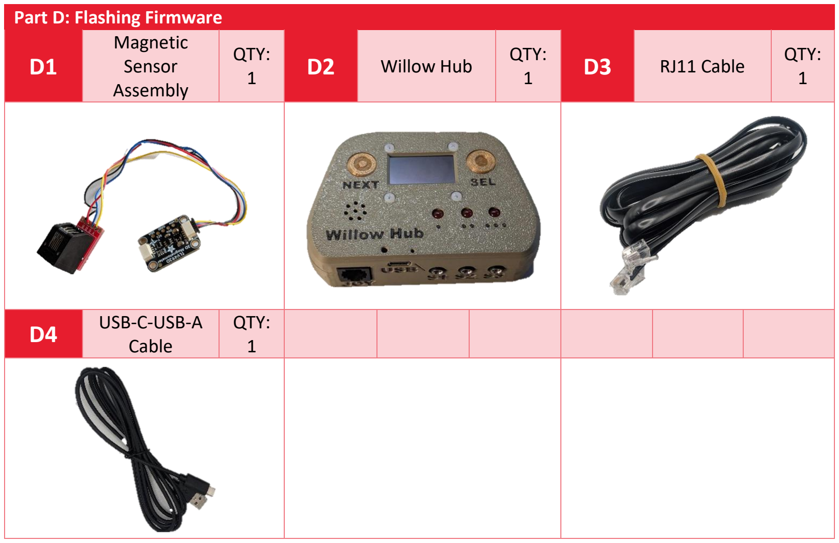
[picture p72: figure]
Part D: Flashing Firmware; Magnetic Sensor Assembly; QTY: 1; Willow Hub; QTY:; RJ11 Cable; USB-C-USB-A Cable

Files available at https://github.com/makersmakingchange/Willow-Joystick Page 17 of 58

## MAKER GUIDE

Files available at https://github.com/makersmakingchange/Willow-Joystick Page 18 of 58

Part E: Joystick Assembly
E1 Inner Gimbal
1

QTY:
1
E2 | Magnet | QTY:
4
E3 | Inner Gimbal 2 | QTY:
1
E4 | Bearings | QTY:
4
E5 | Gimbal Shield | QTY:
1
E6 | Outer Gimbal | QTY:
2
E7 | Part C
Assembly

QTY:
1
E8 | Sled 1 | QTY:
| | 1

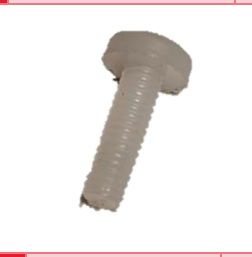
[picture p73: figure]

E9 | M2.5 Machine
Screw, 8 mm

QTY:
4
E10 | M2.5 Nut | QTY: 4 | E11 | Sled 2 | QTY: 1 | E12 | Base | QTY: 1

## MAKER GUIDE

Files available at https://github.com/makersmakingchange/Willow-Joystick Page 19 of 58

E13 | M3 Nut | QTY: 2 | E14 | Pin | QTY: 1 | E15 | Shell | QTY: 1
E16 | Screw, #4,
3/8” Length

QTY:
3
E17 | Any Willow
Topper | QTY: 1

Part F: Optional Components Assembly
F1

Nonslip

Base | QTY: 1 | F2 | Nonslip Foot | QTY: 8 | F3 | Wrist Rest | QTY: 1

F4

Hub Stand
Front | QTY: 1 | F5

Hub Stand

Leg | QTY: 2 | F6 | ¼-20 Bolt | QTY: 1

## MAKER GUIDE

Files available at https://github.com/makersmakingchange/Willow-Joystick Page 20 of 58

### Assembly Guide

Assembly Section
Part A: Hub PCB Assembly

Part B: Hub Enclosure Assembly

Part C: Joystick Prep

Part D: Flashing Firmware

Part E: Joystick Assembly

Part F: Optional Components

## MAKER GUIDE

Part A: Components; LipSync 4 Hub PCB; QTY; Capacitor, 10uF; QTY 1; Resistor R1, 100 Ω,; ¼ W, Through hole; Resistor R2/R3/R4 68 Ω, ¼ W, Through hole; QTY 3; Tactile Buttons S1/S2; QTY 2; Piezo Buzzer PS1240; Male Header, 4; position; Sparkfun QWIIC Adapter; Mono Switch Jacks

Files available at https://github.com/makersmakingchange/Willow-Joystick Page 21 of 58

### Part A: Hub PCB Assembly

## MAKER GUIDE

Files available at https://github.com/makersmakingchange/Willow-Joystick Page 22 of 58

A10 RJ11 Modular
Connector Jack

QTY
1

A11 SeeedStudio
Xiao nrF52840

QTY
1

A12 Male Header, 7
position

QTY
2

A13 Headers, Female, 7
Position

QTY
2

A14 LEDs, 5mm
though hole

QTY
3

A15 Willow Hub LED
Spacer

QTY
1

Part A: Tools
- Soldering iron
- Flush cutters
- Phillips Head Screwdriver
- OPTIONAL: Solderless Breadboard (For soldering male headers to microcontroller)

Part A: Personal Protective Equipment (PPE)
- Safety glasses

## MAKER GUIDE

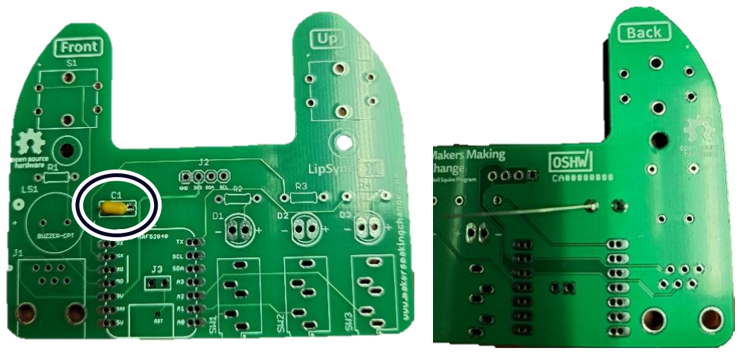
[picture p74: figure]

Files available at https://github.com/makersmakingchange/Willow-Joystick Page 23 of 58

Part A: Hub PCB Assembly Steps
Note that all parts will be inserted onto the side of the PCB labeled “Front”, and all soldering will be done on the side labeled “Back”.

Step A-01: Solder in 10 micro Farad capacitor, C1.
Insert the 10 micro-Farad capacitor (A2) into the position labeled C1 on the PCB (A1). Bend the leads of the capacitor to the side to hold it in place. Solder the capacitor onto the PCB. Once soldered, trim the extra from the leads.

Step A-02: Solder in 100 Ohm resistor, R1.
Insert the 100 Ohm resistor (A3) into the position labeled R1 on the PCB. Bend the leads of the resistor to the side to hold it in place. Solder the resistor onto the PCB. Once soldered, trim the extra from the leads.

## MAKER GUIDE

Files available at https://github.com/makersmakingchange/Willow-Joystick Page 24 of 58

Step A-03: Solder in 68 Ohm resistors, R2, R3, and R4.
Insert the 68 Ohm resistors (A4) into the positions labeled R2, R3, and R4 on the PCB. Bend the leads of the resistors to the side to hold them in place. Solder the resistors onto the PCB. Once soldered, trim the extra from the leads.

Step A-04: Insert, solder, and trim the 4-pin Male header.
Insert the longer pins of the 4-pin male header (A7) into the position labeled J2. Solder it into place and trim the excess from the bottom.

## MAKER GUIDE

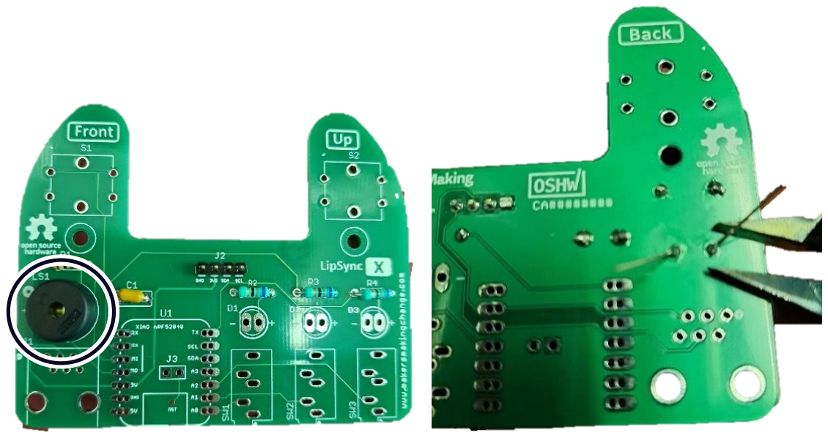
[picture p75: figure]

Files available at https://github.com/makersmakingchange/Willow-Joystick Page 25 of 58

Step A-05: Insert, solder, and trim buzzer.
Insert the buzzer (A6) into the position labeled LS1. If using a buzzer with polarity, make sure the positive lead is in the hole marked with a “+” on the PCB. Note that the Piezo Buzzer PS1240 does not have polarity. Bend the leads to the side to hold the buzzer in place. Solder in place and trim excess from the leads.

Step A-06: Insert, solder, and trim switches.
Insert the two tactile switches (A5) into the positions labeled S1 and S2. Once soldered in place, trim any excess from leads of the switches.

## MAKER GUIDE

Files available at https://github.com/makersmakingchange/Willow-Joystick Page 26 of 58

Step A-07: Insert and solder SparkFun QWIIC Adapter.
Place the SparkFun QWIIC Adapter (A8) on the 4-pin male header (A7) that was attached to J2 in step A-
04. Ensure the pin labels on the adapter matches the pin labels on the Hub PCB. Solder the four pins on the adapter.

Step A-08: Insert and solder switch jacks.
Insert the switch jacks (A9) into the positions labeled SW1, SW2, and SW3. Solder one pin on each switch jack, then check the alignment. If the alignment needs to be changed, reheat the solder joint until the solder melts, then reposition the jack. Once the jacks are positioned properly, solder the remaining pins.

## MAKER GUIDE

Files available at https://github.com/makersmakingchange/Willow-Joystick Page 27 of 58

Step A-09: Solder male headers onto microcontroller.
Insert the short side of the male headers (A12) into the SeeedStudio Xiao nrf52840 microcontroller (A11) from the bottom of the board. To align the male headers and keep them straight when soldering, take the 7-position female headers (A13), and insert the male headers into the female headers across the microcontroller (as shown in the picture on the left).

Alternatively, a solderless breadboard can be used, plug the unsoldered microcontroller and headers into the protoboard and the protoboard will hold the headers in the proper alignment.

Solder the male headers onto the microcontroller, making sure not to connect adjacent pads together with solder. Once soldered, remove the 7-pin female headers from the male headers.

Step A-10: Solder female microcontroller header into PCB.
Insert microcontroller with male headers into the female headers (A13). Insert the female headers into PCB. Solder 1 pin on each header. Check alignment and adjust if necessary. If you need to adjust the alignment, heat the single soldered pin until the solder melts again and adjust the position of the row of headers. Once aligned, solder remaining headers.

## MAKER GUIDE

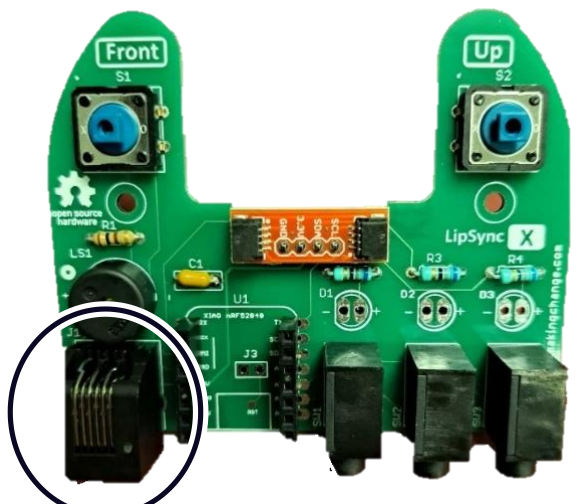
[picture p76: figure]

Files available at https://github.com/makersmakingchange/Willow-Joystick Page 28 of 58

Step A-11: Insert and solder the RJ11 jack.
Insert the RJ11 jack (A10) into the position labeled J1 on the PCB. Solder the six pins into place.

Step A-12: Insert, solder, and trim LEDS.
Insert the three LEDs (A14) into the 3D printed LED Spacer(A15). Ensure the shorter lead of the LED (the negative lead) is on the same side as the flat edge of the LED Spacer. The LED will also have a flat edge matching the flat edge on the spacer.

With the LEDs inserted into the spacer, insert the LEDs into the matching holes in the PCB. The flat side of the LED spacer should be on the left with the rounded side on the right, when looking at the PCB from the front. Solder the LEDs in place and trim the excess from the leads.

## MAKER GUIDE

Files available at https://github.com/makersmakingchange/Willow-Joystick Page 29 of 58

Part A Complete

## MAKER GUIDE

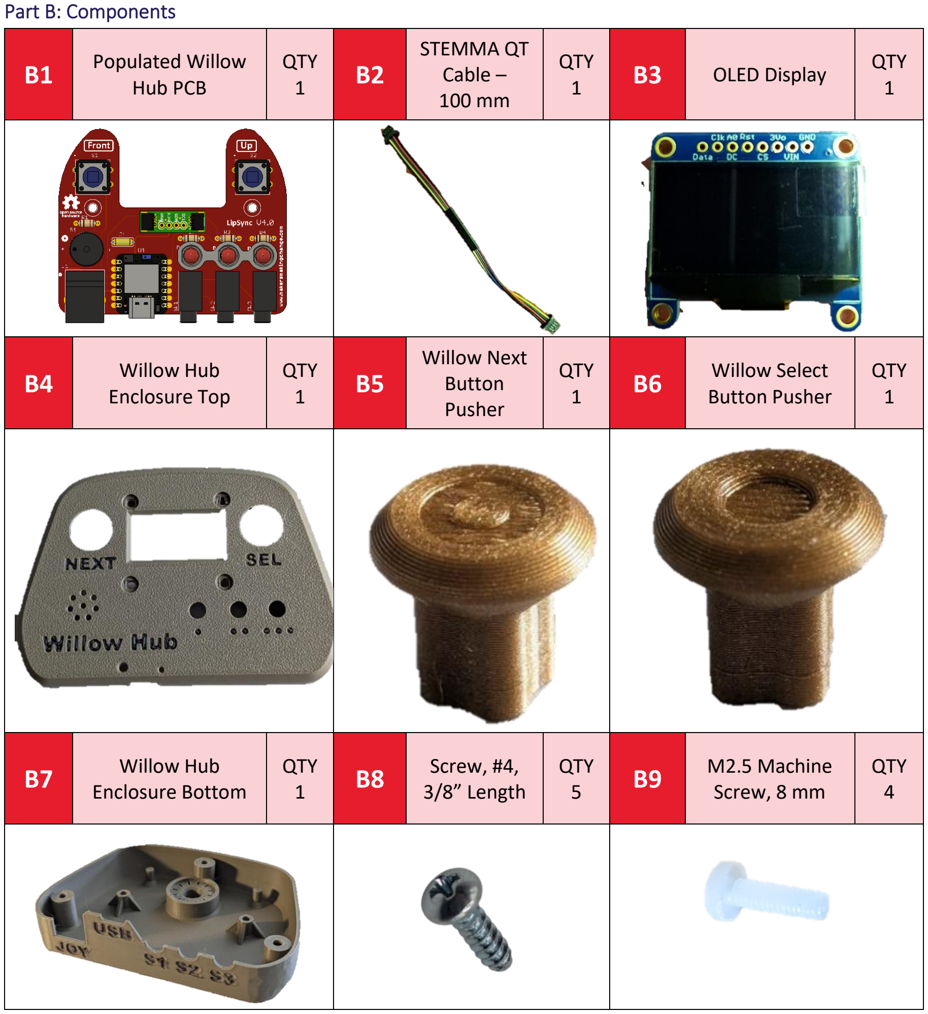
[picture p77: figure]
Part B: Components; Populated Willow; Hub PCB; QTY 1; STEMMA QT Cable – 100 mm; OLED Display; QTY; Willow Hub; Enclosure Top; Willow Next Button Pusher; Willow Select; Button Pusher; Enclosure Bottom; Screw, #4,; 3/8” Length; QTY 5; M2.5 Machine; Screw, 8 mm; QTY 4

Files available at https://github.com/makersmakingchange/Willow-Joystick Page 30 of 58

### Part B: Hub Enclosure Assembly

## MAKER GUIDE

Files available at https://github.com/makersmakingchange/Willow-Joystick Page 31 of 58

B10 | M2.5 Nut | QTY
4
B12 | T-Nut | QTY
1
B13 | Light Pipe | QTY
1

Part B: Tools
- Phillips Head Screwdriver

Part B: Personal Protective Equipment (PPE)
- Safety glasses

## MAKER GUIDE

Files available at https://github.com/makersmakingchange/Willow-Joystick Page 32 of 58

Part B: Assembling Hub Enclosure Steps

Step B-01: Connect Display to Willow Hub Enclosure Top
Peel off the protective film on the Display (B3) and connect it to the Hub Enclosure Top (B4) using four nylon M2.5 machine screws (B9) and four nylon M2.5 hex nuts (B10). Do not overtighten.

Step B-02: Insert the Light Pipe
From the front side, insert the light pipe (B13) into the Hub Enclosure Top.

## MAKER GUIDE

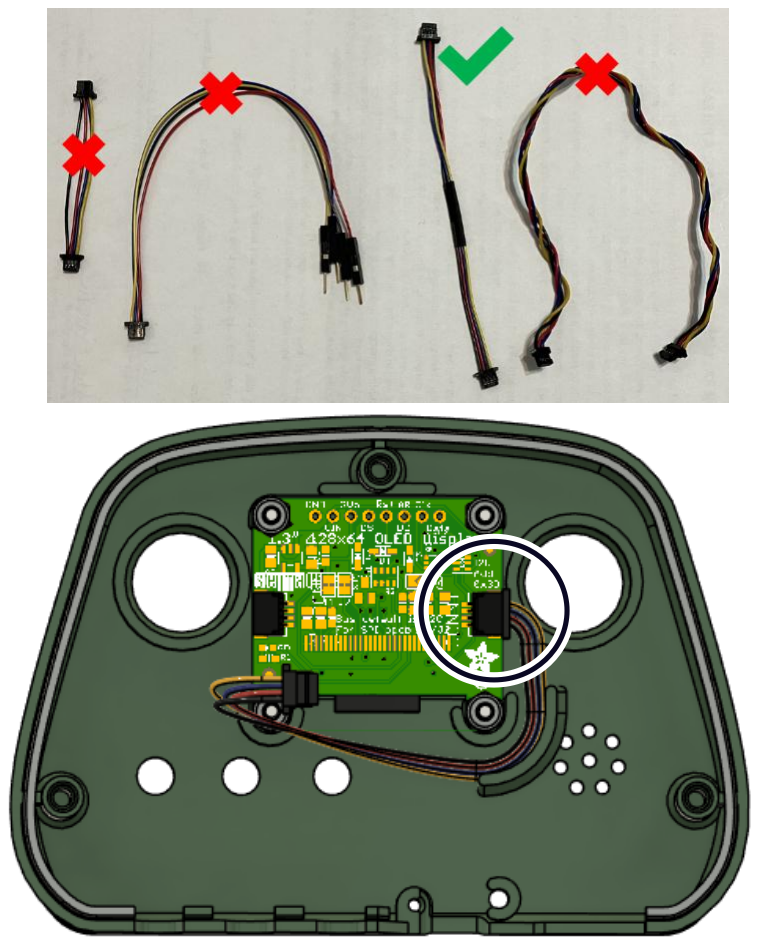
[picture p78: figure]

Files available at https://github.com/makersmakingchange/Willow-Joystick Page 33 of 58

Step B-03: Connect STEMMA / QWIIC Cable to Display
Flip the Hub Top over so the Display is facing down. Connect the 100 mm STEMMA/QWIIC cable (B2) to the port on the right-hand side of the Display as shown. Ensure the holes for the pins in the cable line up with the pins in the port on the PCB. Do not connect the second end of the STEMMA/QWIIC cable to the second port on the screen.

Step B-04: Insert the Tee Nut into the Hub Bottom
Insert the tee nut (B12) into the slots inside the Hub Bottom. A ¼” machine screw or hex bolt can be used to tighten the Tee Nut into place. The nut should sit flush with the enclosure.

## MAKER GUIDE

Files available at https://github.com/makersmakingchange/Willow-Joystick Page 34 of 58

Step B-05: Secure Willow Hub PCB into Hub Bottom
Use two #4 sheet metal screws (B8) to secure the PCB (A1) into the Hub Bottom.

Step B-06: Connect the STEMMA / QWIIC Cable to the QWIIC Adapter on the PCB
Connect the 100 mm STEMMA/QWIIC cable from the display to the QWIIC adapter on the PCB. Again, ensure the holes for the pins in the cable line up with the pins in the port on the PCB.

## MAKER GUIDE

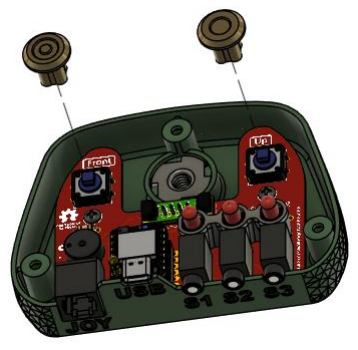
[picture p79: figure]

Files available at https://github.com/makersmakingchange/Willow-Joystick Page 35 of 58

Step B-07: Place the Button Pushers on top of the Buttons
Position the Select Button (B6) and the Next Button (B5) on top of the Buttons on the PCB. The Next Button goes on the left button and has a target shape on the front. The Select Button goes on the right button and has a ring printed on the front.

Step B-08: Position the Hub Top on to the Hub Bottom
Position the Hub Top onto the Hub Bottom, making sure to align the Button Pushers and their LEDs with the corresponding hole.

## MAKER GUIDE

Files available at https://github.com/makersmakingchange/Willow-Joystick Page 36 of 58

Step B-09: Secure the Hub Top and Hub Bottom
Carefully turn the Hub over. Use a #4 sheet metal screw(B8) in each of the three holes to secure the two parts together.

Part B Complete

## MAKER GUIDE

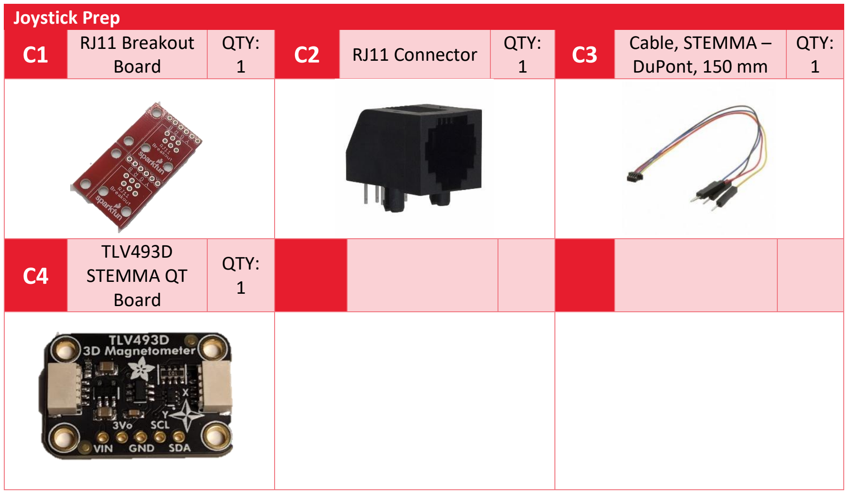
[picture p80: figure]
Joystick Prep; RJ11 Breakout; Board; QTY: 1; RJ11 Connector; QTY:; Cable, STEMMA –; DuPont, 150 mm; TLV493D STEMMA QT Board

Files available at https://github.com/makersmakingchange/Willow-Joystick Page 37 of 58

### Part C: Joystick Prep

Part C: Required Components

Part C: Required Tools and Supplies
- Soldering Iron

Part C: Required Personal Protective Equipment (PPE)Safety glasses

Part C: Joystick Assembly Steps

Step C-01: Snap the breakout boards
Separate the two RJ11 breakout boards (C1) by snapping them apart by hand. Snap off the thin portion with the two mounting holes.

## MAKER GUIDE


Files available at https://github.com/makersmakingchange/Willow-Joystick Page 38 of 58

Step C-02: Solder the RJ11 jack to the RJ11 Breakout Board
Press the RJ11 Jack (C2) into the breakout board so the pins stick out of the numbered side. Solder the six RJ11 pins poking through the board, NOT THE NUMBERED HOLES.

Step C-03: Solder the STEMMA QT Cable to the RJ11 Breakout Board
Insert the DuPont headers on the Stemma-Dupont connector (C3) into the through holes on the RJ11 Breakout Board from the same side as the RJ11 Connector, following the order in the table. Solder in place, and trim the DuPont ends sticking out the back side.
RJ 11 Breakout | STEMMA QT Cable
2 (B) | Black (Gnd)
3 (R) | Red (Vcc)
4 (G) | Blue (SDA)
5 (Y) | Yellow (SCL)

## MAKER GUIDE

Files available at https://github.com/makersmakingchange/Willow-Joystick Page 39 of 58

Step C-04: Plug Stemma Cable into Magnetic Sensor
Take the stemma cable that is soldered to the RJ11 jack and plug it into the left side of the magnetic sensor board (C10) when looking at it with the text at the top, right side up.

## MAKER GUIDE

Flashing Firmware D1; Magnetic Sensor Assembly; QTY: 1; Willow Hub; QTY:; RJ11 Cable; USB-C-USB-A Cable

Files available at https://github.com/makersmakingchange/Willow-Joystick Page 40 of 58

### Part D: Flashing Firmware to Willow

Part D: Required Components

Part D: Required Tools and Supplies
- Computer with Arduino IDE to flash firmware

Step D-01: Connect the Willow Joystick to The Hub
Plug in the Joystick (D1) to the Hub (D2) using the RJ 11 Cable (D3).

Step D-02: Connect the Willow Hub to the Computer
Plug in the Hub (D2) to a computer via USB Cable (D4).

Step D-03: Setup Arduino IDE on Computer
1. Download Arduino IDE for your operating system at https://www.arduino.cc/en/software
2. Install the Arduino IDE.

Step D-04: Setup Arduino IDE for Seed Studio Xiao nRF52840 Development Board
1. Open Arduino IDE.
2. Click on File -> Preferences.
3. Locate the text field that says Additional Boards Manager URLs beside it.
4. Copy and paste the following link into the field as a new line: https://files.seeedstudio.com/arduino/package_seeeduino_boards_index.json
3. Click on OK.
5. Restart the Arduino IDE.
6. Open the Boards Manager option from the Tools-> Board-> Boards Manager...,

## MAKER GUIDE

Files available at https://github.com/makersmakingchange/Willow-Joystick Page 41 of 58

7. Search for “Seeed nrf52” and select “Seeed nRF52 Boards” by Seeed Studio.
8. Click Install to install the board.

Step D-05: Install Libraries
1. In the Arduino IDE, go to Tools -> Manage Libraries…
2. For each of the libraries in the table below, search for the name, and click Install. If prompted to install any dependent libraries, click OK.
Name | Author
Adafruit_SSD1306 | Adafruit
ArduinoJson | Benoit Blanchon
TLV493D-A1B6 | Infineon Technologies
Adafruit_TinyUSB | Adafruit
3. Directly download the compressed zip file for the TLV493D-A1B6 Library:
a. https://github.com/Infineon/TLV493D-A1B6-3DMagnetic-Sensor/archive/refs/heads/master.zip (https://github.com/Infineon/TLV493D-A1B6-3DMagnetic-Sensor/archive/refs/heads/master.zip)
4. In the Arduino IDE, go to Sketch -> Include Library -> Add .ZIP Library… When the dialog box opens, navigate to where the library ZIP file was downloaded in the previous step, select it, and press and select the library downloaded in the previous step.

Step D-06: Setup Local Code Directory
1. Download the Firmware_Files from the GitHub Repository: https://github.com/makersmakingchange/Willow-Joystick/blob/main/Build_Files/Firmware_Files/Willow_Firmware.zip (https://github.com/makersmakingchange/Willow-Joystick/blob/main/Build_Files/Firmware_Files/Willow_Firmware.zip)
2. Extract / unzip the folder to a known location.
3. Confirm that you have the following folder structure:
- Willow_Firmware (folder)
- Willow_Firmware.ino
- LSAPI.ino
- LSTest.ino
- LSBLE.h
- LSBuzzer.h
- LSCircularBuffer.h
- LSConfig.h
- LSInput.h
- LSJoystick.h
- LSMemory.h
- LSOutput.h
- LSScreen.h
- LSTimer.h

## MAKER GUIDE

Files available at https://github.com/makersmakingchange/Willow-Joystick Page 42 of 58

- LSUSB.h
- LSUtils.h

Step D-07: Upload the Code to the microcontroller.
1. Open Willow_Firmware.ino with Arduino IDE.
2. Select Seeed Xiao NRF52840 from Tools -> Board -> Seeed NRF52 Boards
3. Connect the Willow using the USB cable to the computer.
4. Select the correct port from Tools -> Port menu.
5. Verify and upload the code.

### Part E: Joystick Assembly

Part E: Required Components Joystick Assembly
E1 Inner Gimbal
1

QTY:
1
E2 | Magnet | QTY:
4
E3 | Inner Gimbal 2 | QTY:
1
E4 | Bearings | QTY:
4
E5 | Gimbal Shield | QTY:
1
E6 | Outer Gimbal | QTY:
2
E7 | Part C
Assembly

QTY:
1
E8 | Sled 1 | QTY:
| | 1


E9 | M2.5 Machine
Screw, 8 mm

QTY:
4

## MAKER GUIDE

Files available at https://github.com/makersmakingchange/Willow-Joystick Page 43 of 58

E10 | M2.5 Nut | QTY: 4 | E11 | Sled 2 | QTY: 1 | E12 | Base | QTY: 1
E13 | M3 Nut | QTY: 2 | E14 | Pin | QTY: 1 | E15 | Shell | QTY: 1
E16 | Screw, #4,
3/8” Length

QTY:
3
E17 | Any Willow
Topper | QTY: 1

Part E: Required Tools and Supplies
- Phillps head screwdriver
- Optional: Sandpaper
- Optional: Wire Strippers
- Optional: Needle Nose Pliers

## MAKER GUIDE

Files available at https://github.com/makersmakingchange/Willow-Joystick Page 44 of 58

Part E: Joystick Assembly Steps

Step E-01: Insert the Magnet
Press the magnets (E2) into one of the inner gimbal prints (E1), it is not important which one. It is important that they are both in the same orientation, attracting each other instead of repelling.

Step E-02: Attach second half of inner gimbal
Press the second half of the inner gimbal (E3) onto the first and squeeze it tight.

## MAKER GUIDE


Files available at https://github.com/makersmakingchange/Willow-Joystick Page 45 of 58

Step E-03: Attach inner gimbal bearings
Push bearings (E4) onto the posts on the inner gimbal assembly.

Step E-04: Attach the Gimbal Shield
Screw the gimbal shield (E5) onto the threads on the inner gimbal.

Step E-05: Add Outer Gimbal
Take both halves of the outer gimbal (E6) and press them around the inner gimbal. Add the bearings (E5) on the bearing posts to secure them in place.

## MAKER GUIDE


Files available at https://github.com/makersmakingchange/Willow-Joystick Page 46 of 58

Step E-06: Add the Magnetic Sensor assembly
Pass the magnetic sensor assembly (E7) through the loop at the bottom of the gimbal assembly.

Step E-7: Press Gimbal into Sled
Press the gimbal into the sled 1 piece (E8), marked by a single dot by the bottom magnet piece. The magnet in the gimbal should be facing the magnet slot in the bottom of sled 1.

## MAKER GUIDE

Files available at https://github.com/makersmakingchange/Willow-Joystick Page 47 of 58

Step E-08: Bolt the magnetic sensor into place
Take 2 of the M2.5 bolts (E9) and pass them through the magnetic sensor and sled from the top. Take two of the M2.5 nuts (E10) and secure the bolts in place. Passing the bolts through from the bottom also works, and some makers have found it easier to assemble this way.

Step E-09: Insert the Sled Magnet
Press a magnet into the slot on the base of the sled 2 prints(E11), the one that the magnetic sensor is not bolted to. Make sure it matches the orientation of the other magnets, so that the gimbal is attracted to the base instead of repelled.

## MAKER GUIDE


Files available at https://github.com/makersmakingchange/Willow-Joystick Page 48 of 58

Step E-10: Attach Second Half of Gimbal
Press the other half of the gimbal into place so that the magnet is fully captured. Use two of the M2.5 bolts (E9) and nuts (E10) through the magnetic sensor to secure the second half of the gimbal in place. Zip ties can be used to temporarily hold together the sled magnet section while inserting the bolts, but make sure to remove it after this step.

Step E-11: Insert the M3 Nuts
Take the two M3 nuts (E13) and insert them into the slots on the base (E12) of the joystick.

## MAKER GUIDE


Files available at https://github.com/makersmakingchange/Willow-Joystick Page 49 of 58

Step E-12: Attaching the RJ11 Jack
Slide the RJ11 jack into the slots on the inside of the base and secure it with the pin (E14). The picture below has the wires with the DuPont headers removed, but it can be assembled with or without the headers.

## MAKER GUIDE

Files available at https://github.com/makersmakingchange/Willow-Joystick Page 50 of 58

Step E-13: Insert the Gimbal
Wind the cable once around the base of the gimbal. Slot the gimbal into the base, with the top and bottom of the gimbal fitting in the octagons on the top and bottom of the base. The tops and bottom of the octagons of both the gimbal and the base have a slot that fit into each other so that the gimbal can only be inserted in one direction.

## MAKER GUIDE


Files available at https://github.com/makersmakingchange/Willow-Joystick Page 51 of 58

Step E-14: Attach the shell to the base
Attach the shell( E15) with 3 #4 sheet metal screws (E16). Be careful to not pinch the cables when attaching the shell.

Step E-15: Attach the topper
Take the chosen topper (E17) from the list of toppers and insert it into the slot on the top of the joystick gimbal. Twist the joystick clockwise to tighten it, or ‘righty tighty’.

## MAKER GUIDE

Files available at https://github.com/makersmakingchange/Willow-Joystick Page 52 of 58

### Part F: Optional Components

Part F: Required Components Optional Components Assembly
F1

Nonslip
Base | QTY: 1 | F2 | Nonslip Foot | QTY: 8 | F3 | Wrist Rest | QTY: 1

F4

Hub Stand
Front | QTY: 1 | F5

Hub Stand

Leg | QTY: 2 | F6 | ¼-20 Bolt | QTY: 1

Part F: Required Tools and Supplies
- Optional: Wrench or screwdriver to attach the bolt to the hub

## MAKER GUIDE

Files available at https://github.com/makersmakingchange/Willow-Joystick Page 53 of 58

Step F-01-A: Build the Non-Slip Base
Take the nonslip base print (F1) and four of the adhesive feet (F2). Remove the adhesive backing from the feet and press them onto the four indents in the bottom of the 3D print.

Step F-01-B: Attach the Non-Slip Base to the Joystick
Place the joystick on the indent on the non-slip foot and use 2 M3 bolts (F3) to attach the foot to the mounting nuts in the joystick.

## MAKER GUIDE


Files available at https://github.com/makersmakingchange/Willow-Joystick Page 54 of 58

Step F-02: Wrist Ramp
Take the wrist ramp 3D print (F4) and four of the adhesive feet (F2). Flip over the ramp and remove the adhesive backing from the feet. Press the feet into the indents in the bottom of the wrist ramp.

Step F-03-A: Clip Legs to Hub Stand
Take the hub stand front print (F5) and two of the hub stand leg prints (F6). Clip the leg prints into the slots on the back of the front print.

## MAKER GUIDE

Files available at https://github.com/makersmakingchange/Willow-Joystick Page 55 of 58

Step F-03-B: Attach Hub Stand to Willow Hub
Rest the Willow hub on the front stand, with the screw holes on the hub resting on the pillars on the front of the hubs stand. Use a ¼-20 bolt (F6) to secure the stand to the hub.

## MAKER GUIDE

Files available at https://github.com/makersmakingchange/Willow-Joystick Page 56 of 58

### Testing

After building the Willow Hub and Joystick, you must verify both units are functioning properly.

### Testing the Willow

1. Does Display turn on?
a. Ensure that the Willow joystick in plugged into the Hub using the RJ11 cable.
i. Ensure that the Willow Joystick light pipe lights up green.
b. If the Hub turns off and does not work, reset the device, and open the serial monitor in Arduino IDE right after resetting to see if one of the STEMMA boards is not being recognised.

Testing Mouse Mode
Refer to the Willow User Guide for instructions on how to connect the Willow to a Host Device and change the operating mode to USB Mouse Mode. When in USB Mouse Mode, ensure moving the joystick moves the mouse cursor. Additionally, test the external switches and buttons on the Hub. Ensure that each external switch and Hub button action are consistent with the following tables.

Testing External Switches
Plug an assistive switch into the external switch jacks and activate the assistive switch. S1 is the left switch, S2 is the center switch, and S3 is the right switch.

The behaviour for each switch and type of activation is outlined in the table below:

Input | Mouse | Gamepad | Menu/Settings Mode
S1 Short Press | Left Click | Button 1 press | Next
S1 Long Press | Start drag mode | Button 3 press | N/A
S1 Very Long Press | Enter settings mode | Enter settings Mode | Exit settings mode
S2 Short Press | Middle Click | Button 5 press | N/A
S2 Long Press | Middle click | Button 6 press | N/A
S2 Very Long Press | Perform Center Reset | Perform Center Reset | N/A
S3 Short Press | Right Click | Button 2 press | Select menu item
S3 Long Press | Start scroll mode | Button 4 press | N/A
S3 Very Long Press | Middle click | N/A | N/A

Testing Hub Buttons
Ensure the following behaviours are consistent when pressing the buttons on the Hub.
Willow Hub Button Inputs | Select Short Press | Select Long Press | Select Very Long Press | Next Short Press | Next Long Press | Next Very Long Press | Next and Select
Mouse Behaviour | Left Click | Start Drag Mode | Enter Hub Menu | Right Click | Start Scroll Mode | Middle Click | Next and Select

## MAKER GUIDE

Files available at https://github.com/makersmakingchange/Willow-Joystick Page 57 of 58

Input Feedback
Each LED is designated to a set of inputs:

Left LED •: Next (Hub), S1
Middle LED ••: S2
Right LED •••: Sel (Hub), S3

The time durations Short, Long, and Very Long for the switch/button inputs are the following:

Short: Less than 1 seconds. Indicated by the respective LED blinking once button is released. Long: Between 1 to 3 seconds. Indicated by the respective LED turning on and staying on. Very Long: 3 seconds or longer. Indicated by the respective LED turning off.

Ensure the LEDs behave as outlined above.

### Troubleshooting

1. Arduino IDE is stuck when uploading code to the board.

You can first try to reset the board by clicking the "Reset Button" once. If that does not work, rapidly click it twice to enter bootloader mode. If that also doesn't work, disconnect the board from the PC, and connect the board again.

2. The board is not showing up as a serial device on Arduino IDE.

You can first try to reset the board by clicking the "Reset Button" once. If that does not work, rapidly click it twice to enter bootloader mode.

3. The Willow plays an error tone and then lists an error in Safe Mode.
a. Disconnect the Hub from power.
b. Wait 15 seconds.
c. Unplug the Willow Interface cable on both ends and plug both ends back in.
d. Reconnect the Hub to power.

If this does not resolve the error, make note of the error code on the Safe Mode menu screen, and refer to the table below:

## MAKER GUIDE

Files available at https://github.com/makersmakingchange/Willow-Joystick Page 58 of 58

Table 1. Willow Error Table - Makers

Error Code | Connection Error Maker Action Display | Joystick Sensor
ERROR-001 | | ● | 1. Check that I2C cables are securely inserted into the magnetic sensor inside joystick. 2. Check that the LipSync interface cable is securely connected on both ends. 3. Confirm the LipSync Interface Cable is the right type. 4. Check that the RJ11 Connector board inside the joystick has all wires connected.
ERROR-002 | ● | | Check that I2C cable is securely inserted into Display within Hub. Check that I2C cables are securely inserted into each sensor inside joystick.
ERROR-003 | ● ●

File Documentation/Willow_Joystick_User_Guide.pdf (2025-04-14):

V1.0.0 | April 2025

## Willow Joystick

## USER GUIDE


© 2025 by Neil Squire. (https://neilsquire.ca/)
This work is licensed under the CC BY SA 4.0 License: http://creativecommons.org/licenses/by-sa/4.0
Files available at https://github.com/makersmakingchange/Willow-Joystick | Page 1 of 44

### Overview

This document contains the necessary information to use the Willow Joystick, a low force magnetic joystick designed for users with limited finger mobility and strength.

## USER GUIDE

Files available at https://github.com/makersmakingchange/Willow-Joystick | Page 2 of 44

## Contents

Overview | 1
Introduction | 4
Features | 4
Joystick Features | 4
Hub Features | 6
Specifications | 8
Compatibility | 8
Usage | 9
Initial Setup | 9
Connecting to Host Device | 13
Powering the Device | 13
Setting Up Host Device | 18
Operating the Willow | 21
How to Perform Willow Inputs | 21
USB & Wireless Mouse Mode | 22
USB Gamepad Mode | 24
USB Gamepad Mode connected to an Android Smart Phone or Tablet | 25
Mapping Summary | 26
The Hub Menu | 28
Accessing the Hub Menu | 28
Navigating the Hub Menu | 28
Hub Menu Options | 28
Adjusting the Willow | 30
Changing the Cursor Speed | 33
Changing the Scroll Speed | 33
Changing the Light Brightness | 34
Changing the Sound Mode | 35
Input-Output Mapping | 35
Changing Settings Through the Serial Interface (API) | 35
Storage | 35
Care | 35
Cleaning the Willow | 36
Troubleshooting | 37

## USER GUIDE

Files available at https://github.com/makersmakingchange/Willow-Joystick | Page 3 of 44
Error Codes | 38
Contacting Support | 39
Disposal | 39
Appendix A: Serial Interface (Application Programming Interface) | 39
Serial Interface Setup | 39
Serial Settings | 39
Sending Commands | 39
API Format Willow Command List | 40

## USER GUIDE


Files available at https://github.com/makersmakingchange/Willow-Joystick | Page 4 of 44

### Introduction

The Willow is a low force joystick, developed from the magnetic gimbal used in the LipSync. The device allows users with limited strength and range of motion to use a joystick for computer access and gaming.

### Features

Joystick Features

Figure 1:Willow base showing mounting nuts (left), Willow with nonslip base attached (right)

## USER GUIDE

Files available at https://github.com/makersmakingchange/Willow-Joystick | Page 5 of 44

Topper: The Willow has a swappable topper that can be unscrewed and replaced depending on the user’s preference.

Orientation Arrow: This arrow on the enclosure of the Willow Joystick points towards the ‘up’ direction, allowing the user to orient themselves while using the joystick.

Cable Jack: The Willow Hub plugs into this port using the Willow Interface Cable.

Mounting Nuts: The Willow Joystick has two built in M3 nuts that can be used to connect either a ¼-20 mounting adapter, a RAM B mounting adapter, or a nonslip base.

Non-Slip Feet: The optional non-slip base has 4 non-slip feet that prevent the Willow Joystick from sliding around on the table during normal use.

## USER GUIDE


Files available at https://github.com/makersmakingchange/Willow-Joystick | Page 6 of 44

Hub Features

## USER GUIDE

Files available at https://github.com/makersmakingchange/Willow-Joystick | Page 7 of 44

Hub Display: The Hub Display allows the users to make quick adjustments to device settings, calibrate the joystick, and change the operating mode. It also displays mode and version information upon startup.

Next & Select Buttons: The Next and Select Buttons on the Hub allows a support person to access the Hub Menu without the need to use the assistive switch ports.

Feedback Speaker: The Feedback Speaker gives auditory feedback through beeping tones. The sound can be turned on or off through the Hub Menu.

Feedback Lights: The Feedback Lights give visual feedback through flashing on input durations. Each light represents a specific set of inputs.

Operating Mode Indicator: The Operating Mode Indicator is used to show whether the device is in USB Mouse, Wireless Mouse, or USB Gamepad mode.

Microcontroller Reset: The Microcontroller Reset hole allows access to the reset pin on the microcontroller using a paperclip or similar sized object.

Mounting Connection: The Hub can be mounted in view beside the host device screen so that it is easy to see/hear the feedback and read the Menu Screen when adjusting settings. The ¼-20 threads are the same as a standard camera mount.

Joystick Port: The Willow Joystick plugs into this port using the Willow Interface Cable.

USB Port: This port provides the device with power and can also be the direct connection to the host device.

Assistive Switch Ports: Up to 3 assistive switches with 3.5 mm audio plugs can be connected to the Willow Hub.

## USER GUIDE

Files available at https://github.com/makersmakingchange/Willow-Joystick | Page 8 of 44

### Specifications

Item | Willow Joystick | Willow Hub
Size (Length x Width x Height) [mm] | 87 mm x 75 mm x 42 mm | 104 mm x 29 mm x 72 mm
Mass [g] | 93 g | 90 g
Power Consumption | ~0.1 W (20 mA @ 5 V)
Joystick Angular Range | ± 7.5° | N/A
Joystick Movement Range | ± 5mm | N/A
Operating Force | 25 grams force | N/A

### Compatibility

The Willow is compatible with host devices that support a USB Mouse, a Bluetooth Mouse, or a USB-HID Gamepad. This includes Windows, macOS and Linux computers, most Android and Windows phones and tablets, and Apple iOS phones and tablets with iOS13 and iPadOS. Not all mobile phones and tablets support external pointing devices like the Willow or other mouse replacements. Check with the manufacturer before purchasing. Look to see if your device supports “USB OTG HID” or “Universal Serial Bus On-the-Go Human Interface Device” profile.

Operating
System

Compatibility per Mode
USB Mouse | Wireless Mouse | USB Gamepad
| Android | 1 | 1
| iOS²
| iPadOS
| Windows
| macOS
| Linux
| Windows

Phone/Tablet

Desktop

1 Only with devices with USB OTG HID (Universal Serial Bus On-The-Go Human Interfere Device) 2 Only for iOS13+ and iPadOS.

## USER GUIDE


Files available at https://github.com/makersmakingchange/Willow-Joystick | Page 9 of 44

## Usage

Initial Setup
This section outlines the necessary and optional steps to set up the Willow Joystick.
1. Mount the Willow Joystick
The first step to mounting the Willow Joystick is to determine where it is to be mounted. The joystick can be mounted on a mounting arm, or it can be placed on a table or other flat surface.

When mounting on a mounting arm, one of the mounting arm adaptors can be attached to the joystick using two M3 screws to attach either a ¼-20 camera thread or a RAM B ball mount to the joystick. When mounting on a desk, the same M3 nuts can be used to attach a nonslip foot plate to the bottom of the joystick to prevent it from sliding around during normal use.

Figure 2: Willow Joystick with 1/4-20 Adaptor (left), Nonslip Base (right)

For some users, the height of the Willow Joystick while placed on the table may make it difficult to use. The Willow includes print files and design files for a parametric wrist rest, which is a ramp with a variety of adjustable parameters to create a custom ramp to raise the user’s wrist to a level that is more comfortable.

## USER GUIDE


Files available at https://github.com/makersmakingchange/Willow-Joystick | Page 10 of 44
2. Mount the Willow Hub
The Willow Hub should be mounted or placed in a location within view of the user. Ideally the Willow Hub is located within 1 m of the user, near the host device screen. Like the Joystick, the Willow Hub has a female ¼”-20 UNC threaded mounting connection on the back side of the device.

Using a mounting arm
1. Position your mounting arm so it does not interfere with your view of the screen so that the ¼-20 threaded end sits where you want to mount the Hub.
2. Connect the Hub to the Mounting Arm using the ¼-20 threads.
3. Adjust your mounting arm as needed to position the Hub specifically where you want it to be.

Mounted on a desk or table
1. Clear a space for the Hub to sit on the desk near the monitor. The Hub can rest on the back surface or can be connected to an optional desktop stand.
2. If using, mount the Hub in the stand with a ¼-20 bolt.
3. Place the Hub in the cleared off spot.

## USER GUIDE


Files available at https://github.com/makersmakingchange/Willow-Joystick | Page 11 of 44
3. Connect the Willow Joystick to the Willow Hub
The Willow Joystick must be connected to the Willow Hub using the Willow Interface Cable. Attach one end of the cable to the Hub Port on the Willow Joystick. Attach the other end of the cable to the Joystick Port on the Willow Hub, which is labelled “JOY”. Ensure the cable is routed and secured appropriately to keep it from getting snagged or damaged.

Ensure you plug in the Willow Interface Cable in the correct orientation. The tab side of the plug inserts into the narrower side of the outlet.

If the cable is damaged or a different length is required, the Willow Interface Cable is a standard RJ11 phone cable.

## USER GUIDE


Files available at https://github.com/makersmakingchange/Willow-Joystick | Page 12 of 44
4. Optional: Connect Assistive Switches to the Willow Hub
The Willow Hub has three 3.5 mm ports for connecting external assistive switches. The three ports are labelled S1, S2, and S3. You can plug a switch into any combination of, or all the assistive switch ports as needed.

By default, an assistive switch attached to S1 will do a left click, and an assistive switch attached to S3 will do a right click when in mouse mode. A full summary of the Assistive Switch mapping is available in the Assistive Switch Inputs section.

After completing these steps, the Willow is now ready to connect to the Host Device which is outlined in the next section.

## USER GUIDE


Files available at https://github.com/makersmakingchange/Willow-Joystick | Page 13 of 44
5. Optional: Set Up Wrist Ramp
Included with the print and design files for the Willow is a 3D printable wrist ramp. The wrist ramp is designed to raise the user’s hand to a level that they can comfortably use the Willow. If the provided ramp is the wrong size or otherwise uncomfortable, the design files for the ramp are provided, and all the design parameters are parametric, allowing the maker to size them to the user. A custom ramp can also be created out of foam.

### Connecting to Host Device

The Host Device is the computer, tablet, laptop, smartphone, or other device that the user wants to control with the Willow. How the Willow is connected will depend on the type of Host Device and whether the Willow is intended to operate as a USB Mouse, USB Gamepad, or Wireless Bluetooth Mouse.

The Willow requires both a communication connection and a power connection.

To connect to the Host Device, you must first ensure that the device is powered, then check which mode it is in and change through the menu if required.

Powering the Device
The Willow requires an external power source. Users can draw power from the host device (except on iOS devices) or use a USB wall charger or power bank via the USB port on the Hub. The Willow is provided with a USB-C to USB-A cable. Depending on the host device and operating mode, a suitable adapter or USB-C to a specific USB plug type cable may be required.

The general set-up will look like the following for any operating mode, where the required connection or adapter will vary depending on how you want to connect the device. When in Wireless mode, the Willow can be connected directly to any power source.

## USER GUIDE


Files available at https://github.com/makersmakingchange/Willow-Joystick | Page 14 of 44

See the below table for compatible power connection types for common host devices.

Common Host Devices | Power Connections | Common Cables for Direct Connection to Host Device | Common Adapters for Splitting to External Power
Direct to Host Device | Using External Power Source
Windows PC | USB-C to USB-C | Male USB 2 to Dual Female (https://www.amazon.ca/Female-Splitter-Power-Extension-Adapter/dp/B07CKQSTCB?hvadid=578878818136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)
| USB-A to USB-C | USB 2 Splitter (https://www.amazon.ca/Female-Splitter-Power-Extension-Adapter/dp/B07CKQSTCB?hvadid=578878818136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)
Mac | USB-C to USB-C | USB-C Splitter (https://www.amazon.ca/Adapter-Charging-Compatible-Samsung-Galaxy/dp/B09CTSHZR7?hvadid=579290833365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)
Android Phone/Tablet | USB-C to USB-C | USB-C Splitter (https://www.amazon.ca/Adapter-Charging-Compatible-Samsung-Galaxy/dp/B09CTSHZR7?hvadid=579290833365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)
| USB-C to USB-B Micro | Male USB-B Micro to Dual Female USB 2 Splitter (https://www.amazon.ca/dp/B06WPBSWHB?s=electronics&sp_csd=d2lkZ2V0TmFtZT1zcF9kZXRhaWw)
Apple Phone/Tablet | USB-C to Lightning | Lightning to USB 3 Adapter (https://www.apple.com/ca/shop/product/MK0W2AM/A/lightning-to-usb-3-camera-adapter)
| USB-C to USB-C | USB-C Splitter (https://www.amazon.ca/Adapter-Charging-Compatible-Samsung-Galaxy/dp/B09CTSHZR7?hvadid=579290833365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)
More detailed instructions for how to connect the Willow to various host devices in different modes are found below.

Once the Willow is connected to power, it will turn on automatically. The Hub will emit a start-up tone, and the Hub Display will show the current code version and the current operating mode. The Joystick must be plugged into the Hub for the device to fully power on.

Changing the Operating Mode
The Willow can operate in three modes: USB Mouse, Wireless Bluetooth Mouse, and USB Gamepad. The current operating mode is indicated on the display on startup and by the colour of the Operating Mode Indicator. The default operating mode is USB Mouse.
Operating Mode | Operating Mode Indicator
USB Mouse | Purple

## USER GUIDE


Files available at https://github.com/makersmakingchange/Willow-Joystick | Page 15 of 44
Wireless Mouse | Blue (Solid = connected, flashing = searching)
USB Gamepad | Yellow
To change the operating mode, use the Hub Display menu. For an explanation on how to perform the given inputs, see the section on How to Perform Willow Inputs. To enter and navigate the menu:
Output | Input
Assistive Switch | On Hub Button
Enter/Exit menu | S1 very long press (>3 seconds) | Select very long press (>3 seconds)
Enter/Exit Menu | Simultaneous Press of S1 and S3 | Simultaneous Press of Next and Sel
“Next” – goes to next option | S3 | Next
“Select” – Selects the current option | S1 | Sel

Connecting in USB Mouse Mode
Using the Hub Menu, ensure you are in USB Mouse mode. This is the default setting when the device is first programmed. When in USB Mouse mode, the operating mode indicator will turn purple.

Plugging Directly into a Computer or Laptop

If you have the appropriate cable, the Willow can be directly plugged into the device’s USB port to work in USB Mouse or Gamepad mode. The Hub port requires a USB-C plug, and most host devices will require either USB-A or USB-C plug types.

The order in which you connect the USB cables may affect how the Willow works. Connect the cables in the following order:

1. Connect the Willow Interface Cable to the Willow Joystick and Willow Hub.
2. Connect a cable with a USB-C connection to the Willow Hub, and the other end (either USB-C or USB-A) to the host device.
3. Wait 3 seconds for the Willow to initialize. Initialization is complete when the Hub Display reads “Ready for use”.

## USER GUIDE


Files available at https://github.com/makersmakingchange/Willow-Joystick | Page 16 of 44

Plugging Directly into an Android Mobile Device
The Willow can be directly plugged into the device’s USB port to work in USB Mouse or Gamepad mode using the appropriate cable and/or adapter. The Hub port requires a USB C plug, and most host devices will require either USB-C, USB-B Micro, or USB-A plug types.
1. Connect the Willow Interface Cable to the Willow Joystick and Willow Hub.
2. Connect a cable with a USB-C connection to the Willow Hub, and the other end (depending on the device) to the host device.
3. Wait 3 seconds for the Willow to initialize. Initialization is complete when the Hub Display reads “Ready for use”.

Plugging into an iOS or Android Mobile Device with an External Power Source
The Willow cannot draw power from an iOS device and therefore must have a powered USB hub or powered USB splitter to connect between the Willow Hub and iOS device. For an Android mobile device (phone or tablet), using an external power source is optional, but can extend the battery life of your device.

The order in which you connect the USB cables may affect how the Willow works. Connect the cables in the following order if using an external power source:

1. Connect the Willow Interface Cable to the Willow Joystick and Willow Hub.
2. Connect a USB-C cable to the Willow Hub and plug the other end into a USB Splitter or Powered Adapter. Connect the USB Splitter to power with the required cable.
3. Connect the other end of the splitter/adapter into the host device (USB-C or USB-B micro).

## USER GUIDE


Files available at https://github.com/makersmakingchange/Willow-Joystick | Page 17 of 44
4. Wait 3 seconds for the Willow to initialize. Initialization is complete when the Hub Display reads “Ready for use”.

Note that to use the Willow with an iOS device, the device must have AssistiveTouch within the Accessibility Settings turned on. Instructions for this are in the Set Up Host Device Section.

Connecting in Wireless Mouse Mode
Using the Willow as a Wireless Bluetooth Mouse requires a Bluetooth-compatible Host Device and an external power source. In Wireless Mouse Mode, the Willow can be paired by a different host device, a USB Power Bank, or a USB wall power adapter.

The Willow will need to be initially paired with the Host Device using the Host Device interface, which will likely require additional assistance. Once the Willow is paired to a Host Device, it will automatically reconnect if the power is turned off and on again.

Use the following steps to connect in Wireless Mouse Mode:

1. Connect the Willow Interface Cable to the Willow Joystick and Willow Hub.
2. Connect the Willow Hub to a power source through the USB-C cable.
3. Wait 3 seconds for the Willow to initialize. Initialization is complete when the Hub Display screen reads “Ready for use”.
4. If necessary, activate the Hub Menu and change the operating mode to BT Mouse mode.

Pairing the Willow to a Bluetooth-Compatible Host Device
When the Willow is in Wireless Mouse mode, it will automatically advertise itself as “Willow”. The Operating Mode Indicator will flash blue indicating it is ready to pair.

On the host device:
1. Confirm that Bluetooth is activated.
2. Navigate to Settings > Bluetooth
3. Tap on Willow to pair.
4. A Connected message will show beside the device name when it successfully connects.

Once paired, the indicator will remain a solid blue.

## USER GUIDE


Files available at https://github.com/makersmakingchange/Willow-Joystick | Page 18 of 44

Note: that when pairing with an iOS device, the device must have AssistiveTouch within the Accessibility Settings turned on to use the paired Willow. Instructions for this are in the Set Up Host Device Section.

Reconnecting the Willow to a Bluetooth-Compatible Host Device
If the Willow is powered off, it will automatically reconnect to the previously paired Bluetooth Host Device when the Willow is powered on again.

Disconnecting the Willow from a Bluetooth-Compatible Host Device
If you no longer wish to use the Willow with a particular device, you will need to disconnect the Willow using the Bluetooth settings on the Bluetooth Compatible Host Device.

Connecting in USB Gamepad Mode
Gamepad mode is available through USB connection only and is compatible with any device that supports USB-HID connection. The Willow Hub can be connected directly to a Computer, Laptop, or Android device in the same way as in USB Mouse Mode.

Using the menus through the Hub Display, ensure you are in Gamepad mode. USB Mouse mode is the default setting when the device is first programmed. When in Gamepad mode, the operating mode indicator will turn yellow.

When connecting to the Xbox Adaptive Controller (XAC), the XAC must be connected and paired with a device for the Willow to receive power and function. The Willow Hub can be plugged into either the left or right USB Joystick inputs. The following table links to resources for using the XAC and configuring controllers in Steam, a gaming platform.

QR Code Resource
Adaptors for XAC compatibility with other systems. (https://www.makersmakingchange.com/s/managed-content-news/assistive-technology-in-gaming-MCTUYK7YHG6NFNTHPTBE7U5J4RTM)

Guide for remapping Willow inputs with the XAC. (https://www.youtube.com/watch?v=gm4w4qXaDm8)

Guide for configuring a controller in Steam. (https://partner.steamgames.com/doc/features/steam_controller/getting_started_for_players)

Setting Up Host Device
There may be settings on the host device that enable the Willow to be used more easily and/or more effectively.

## USER GUIDE

Files available at https://github.com/makersmakingchange/Willow-Joystick | Page 19 of 44

Enable On-Screen Controls – Enables access to functions that usually require physical access to the device.

Enable On-Screen Keyboard – Provide a keyboard for inputting characters.

Adjust Host Device Cursor Size – Increasing cursor size can make it easier to see.

Adjust Host Device Cursor Speed – The cursor speed is adjustable on some devices. The cursor speed can also be adjusted separately on the Willow.

Adjust Host Device Double Click Speed – Increasing the allowable delay between clicks may make it easier to input a double click.

## USER GUIDE


Files available at https://github.com/makersmakingchange/Willow-Joystick | Page 20 of 44

Enable On-Screen Controls

The assistant menu is a floating onscreen menu that allows access to important functions that cannot be accessed without physically touching the device, like the home button, back, zoom in and out, screen capture, volume, and restart.

On Android devices, turn on the Assistant Menu/ Accessibility Menu by going to Setting → Accessibility → Dexterity and Interaction → Assistant Menu

On iOS devices, turn on AssistiveTouch by going to Settings → Accessibility → Touch → AssistiveTouch

On some devices, a swiping action is required to unlock it. This can be avoided by turning off screen lock. Alternatively, applications such as Keep Screen On can be downloaded from the Android Play store to prevent the phone from going to sleep. However, this will drain your phone battery faster.

Android device | iOS device

## USER GUIDE


Files available at https://github.com/makersmakingchange/Willow-Joystick | Page 21 of 44

QR Code Resource
iPhone accessibility features. (https://support.apple.com/en-ca/guide/iphone/iph3e2e4367/ios)

Android accessibility features. (https://www.android.com/intl/en_ca/accessibility/)

Windows accessibility features. (https://support.microsoft.com/en-us/windows/discover-windows-accessibility-features-8b1068e6-d3b8-4ba8-b027-133dd8911df9)

Mac accessibility features. (https://support.apple.com/en-ca/guide/mac-help/mh35884/mac)

### Operating the Willow

The Willow has a range of inputs including the joystick, optional assistive switches, and the buttons on the Hub. Using these inputs, the user, or support person, can adjust settings, change modes, and access the various output actions available in each mode.

How to Perform Willow Inputs
The Willow has a range of inputs available through the joystick, assistive switches, and Hub buttons. This section outlines how to perform each input type.

Moving The Joystick
To use the joystick, move the joystick in the desired direction. The further the joystick is moved, the faster the cursor will move. When the joystick is released, it will return to its resting position.

Using External Assistive Switches
Up to three External Assistive Switches with standard 3.5 mm audio jack connections can be used with the Willow to provide input. The Assistive Switches are connected to the Willow Hub via the external switch ports labeled S1, S2, and S3.

Using the Hub Buttons
The Hub Buttons provide two functions: they provide a way to navigate the Hub Menu, and they enable a support person to perform the same actions as the assistive switches without having to use the user’s assistive switches.

To activate the Hub Buttons, simply press down and then release on one or both of the round buttons on the face of the Hub. Next and Select (Sel) are both mapped to S1 and S3, respectively.

## USER GUIDE

Files available at https://github.com/makersmakingchange/Willow-Joystick | Page 22 of 44

Timed Inputs
The amount of time that any input (switches/buttons) is held before being released will trigger different actions.

Short: Less than 1 second. Indicated by the respective LED blinking once.
Long: Between 1 to 3 seconds. Indicated by the respective LED lighting up and staying on. Very Long: 3 seconds or longer. Indicated by the respective LED turning back off.

For each input in regular operating modes, a specified Feedback Light will indicate the input duration. The feedback lights are designated to the inputs as follows:

Left Light •: S1, Select (Sel) button on Hub
Middle Light ••: S2
Right Light •••: S3, Next button on Hub

For example, to perform a Very Long S1, press and hold the assistive switch connected to S1. After you hold the switch for 1 second, the Right Feedback Light on the Hub will turn on. After 3 seconds, the Right Feedback Light will turn off. Release the switch to trigger a Very Long S1.

USB & Wireless Mouse Mode
In either USB or Wireless Mouse Mode, the joystick controls the cursor, and the assistive switches are mapped to different mouse button clicks.

Mouse Mode Functions

Function | Description
Moving the Cursor | Performs the same function as moving a mouse to move the pointer/cursor on the screen.
Left Click | Performs the same function of the left click on a mouse
Right Click | Performs the same function of the right click on a mouse
Middle Click | Performs the same function of the scroll wheel push on a mouse
Drag Mode | Will mimic the left click on the mouse held down to drag items on the screen such as folders
Scroll Mode | Keeps the mouse stationary and the joystick can control the scroll speed

Moving the Cursor
To move the cursor, move the joystick in the desired direction. The further the joystick is moved, the faster the cursor will move. Releasing the joystick will return it to the center position and the cursor will stop moving.

If the cursor continues to move after the joystick is released see the

## USER GUIDE

Files available at https://github.com/makersmakingchange/Willow-Joystick | Page 23 of 44

Troubleshooting Section: page 37.

Left Clicking
To do a left click, do a short press of the Hub “Select” button or S1.

Right Clicking
To do a right click, do a short press of the Hub “Next” button or S3.

Double Clicking
To do a double click, do two short press of the Hub “Select” button or S1. The left LED will blink once for each press.

It may be helpful to decrease the double click speed on the host device.

Middle Clicking
Middle click is used for tasks such as turning the cursor into scroll mode in web browsers and in documents. On a typical mouse, a middle click is accomplished by clicking the scroll wheel. Note that not all mice have a scroll wheel that clicks.

To do a middle click, apply and maintain a very long press of the S3 switch or Hub “Next” button (At least 3 seconds). The right-side LED will turn off once the duration has been reached.

A middle click can also be generated by a short press of S2.

Drag
Drag is used for tasks such as repositioning windows or icons or selecting objects such as text. On a typical mouse, drag is accomplished by pressing and holding the left click. On the Willow, drag is accomplished by starting Drag mode.

To start Drag Mode, apply and maintain long press (between 1 and 3 seconds) of the Hub “Select” button, or a long press of S1.and then release the press. The Left Feedback Light will turn on and stay on once the duration has been reached.

To drag, move the joystick in any direction.

To stop drag mode, apply a short press of S1 or S3.

Vertical Scroll
Vertical scroll is useful for scrolling up and down within documents or webpages. On a typical mouse, this is often controlled by rotating a scroll wheel. On the Willow, vertical scrolling is accomplished by activating Scroll Mode and using vertical motion of the joystick.

To activate Scroll Mode, input long press of S3 (between 1 and 3 seconds). The Right Feedback Light will turn on when the threshold has been reached.

To scroll, move the joystick up or down. The further the joystick is moved, the faster the scroll.

## USER GUIDE

Files available at https://github.com/makersmakingchange/Willow-Joystick | Page 24 of 44

To stop scroll mode, apply a short press of S1 or S3.

USB Gamepad Mode
In Gamepad mode, the Willow inputs are translated to gaming outputs instead of mouse functions. The Willow will act as a gamepad with one joystick and 6 buttons.

In some direct applications, these buttons will have default functions, such as when plugged into the XAC, or plugged into a mobile smart phone. When used with a program such as Steam, the inputs will have to be mapped to the desired outputs to setup the Willow as a controller. Note that while the Willow inputs are set to default outputs with the XAC, you can modify this mapping through the Xbox Accessories App. (https://support.xbox.com/en-CA/help/account-profile/accessibility/customize-adaptive-controller-in-xbox-accessories-app)

Gamepad Mode Functions

Function | Description
Moving the Joystick | Performs the same function as moving a standard joystick or thumbstick in gaming applications.
Button 1 Press | Performs the same function of pressing button 1 on a standard gamepad.
Button 2 Press | Performs the same function of pressing button 2 on a standard gamepad.
Button 3 Press | Performs the same function of pressing button 3 on a standard gamepad.
Button 4 Press | Performs the same function of pressing button 4 on a standard gamepad.
Button 5 Press | Performs the same function of pressing button 5 on a standard gamepad.
Button 6 Press | Performs the same function of pressing button 6 on a standard gamepad.

Moving the Joystick
To move the joystick, move the joystick in the desired direction. The further the joystick is moved, the further the gamepad joystick will move. Releasing the joystick will return it to the center position and the gamepad joystick will return to center.

If the cursor continues to move after the joystick is released see the

## USER GUIDE

Files available at https://github.com/makersmakingchange/Willow-Joystick | Page 25 of 44

Troubleshooting Section: page 37.

Button 1 Press
To do a button 1 press, do a short (less than 1 second) press of S1 or the Hub “Select” button. The button 1 press will be generated when the button or switch is released.

Button 2 Press
To do a button 2 press, do a short (less than 1 second) press of S3 or the Hub “Next” button. The button 2 press will be generated when the button or switch is released.

Button 3 Press
To do a button 3 press, do a long (between 1 and 3 seconds) press of S1 or the Hub “Select” button. The button 3 press will be generated when the button or switch is released.

Button 4 Press
To do a button 4 press, do a long (between 1 and 3 seconds) press of switch S3 or the Hub “Next” button and then release. The button 4 press will be generated when the button or switch is released.

Button 5 Press
To do a button 5 press, do a very long (between 1 and 3 seconds) press of the Hub “Select” button or a short (less than 1 second) press of the S2 switch. The button 5 press will be generated when the button is released.

Button 6 Press
To do a button 6 press, perform a long press (between 1 to 3 seconds) of S2. The button 6 press will be generated when the long press of S2 is released.

USB Gamepad Mode connected to an Android Smart Phone or Tablet
When connected to a smart phone in Gamepad Mode, the Willow acts similar to switch scanning but uses the joystick to move the scanning target.
Function | Description
Moving the Scanning Target | Moves the target selector around the screen one target at a time, side to side, or up and down.
Select | Performs the same function as tapping on the selected field.
Back | Performs the same function as the back button on an Android smart phone.

Moving the Scanning Target
To move the scanning target, move the joystick in one of the four cardinal directions: up, down, left, or right. If the joystick is held in the chosen direction, the selection field will move in that direction, highlighting the different apps or selections as it goes.

Select
To select the highlighted field, do a short press of the Hub “Select” button or assistive switch S1. The Select function will be performed when the short press is released.

## USER GUIDE

Files available at https://github.com/makersmakingchange/Willow-Joystick | Page 26 of 44

Back
To use the Back function, do a short press of the Hub “Next” button or assistive switch S3. The Back function will be performed when the short press is released.

## USER GUIDE

Files available at https://github.com/makersmakingchange/Willow-Joystick | Page 27 of 44

Mapping Summary
The overall mapping of the Willow inputs and feedback features is as follows:

Feedback Features

Each Feedback Light is designated to a set of inputs:
Left Light •: S1, Select (Sel) Hub button
Middle Light ••: S2
Right Light •••: S3, Next Hub button

The time durations Short, Long, and Very Long for the switch/button inputs are the following:

Short: Less than 1 second. Feedback Light blinks once when released.

Long: Between 1 to 3 seconds. Feedback Light turns on and stays on.

Very Long: 3 seconds or longer. Feedback Light turns back off.

## USER GUIDE

Files available at https://github.com/makersmakingchange/Willow-Joystick | Page 28 of 44

Assistive Switch Inputs
Willow Assistive Switch Inputs | Hub Menu | Mouse (PC or Mobile) | Gamepad
PC | Mobile (Android) | XAC (Left USB) | XAC (Right USB)
S1 Short Press | Select | Left Click | Button 1 | Select | X1 (Left Stick Up) | View
S1 Long Press | N/A | Start Drag Mode | Button 3 | Select | Left Stick Press | Right Stick Press
S1 Very Long Press | Exit Hub Menu | Enter Hub Menu | Enter Hub Menu | Enter Hub Menu | Enter Hub Menu | Enter Hub Menu
S2 Short Press | N/A | Middle Click | Button 5 | Back | A | X
S2 Long Press | N/A | N/A | Button 6 | N/A | B | Y
S2 Very Long Press | N/A | Perform Center Reset | Perform Center Reset | Perform Center Reset | Perform Center Reset | Perform Center Reset
S3 Short Press | Next | Right Click | Button 2 | Select | X2 (Left Stick Down) | Menu
S3 Long Press | N/A | Start Scroll Mode | Button 4 | N/A | Left Bumper | Right Bumper
S3 Very Long Press | N/A | Middle Click | N/A | Select | N/A | N/A

Chorded Inputs (Simultaneous short press)
S1 and S3 | Exit Hub Menu | Enter Hub Menu

Enter Hub
Menu

Enter Hub
Menu

Enter Hub
Menu

Enter Hub
Menu

Hub Button Inputs
Willow Hub Button Inputs | Hub Menu | Mouse (PC or Mobile) | Gamepad
PC | Mobile (Android) | XAC (Left USB) | XAC (Right USB)
Select Short Press | Select | Left Click | Button 1 | Select | X1 (Left Stick Up) | View
Select Long Press | N/A | Start Drag Mode | Button 3 | Select | Left Stick Press | Right Stick Press
Select Very Long Press | Exit Hub Menu | Enter Hub Menu | Enter Hub Menu | Enter Hub Menu | Enter Hub Menu | Enter Hub Menu
Next Short Press | Next | Right Click | Button 2 | Back | X2 (Left Stick Down) | Menu
Next Long Press | N/A | Start Scroll Mode | Button 4 | N/A | Left Bumper | Right Bumper
Next Very Long Press | N/A | Middle Click | Button 5 | Select | A | X

Chorded Inputs (Simultaneous short press)
Next and
Select | Exit Hub Menu | Enter Hub Menu

Enter Hub
Menu

Enter Hub
Menu

Enter Hub
Menu

Enter Hub
Menu
Note: Default XAC mappings can be modified through the Xbox Accessories App. (https://support.xbox.com/en-CA/help/account-profile/accessibility/customize-adaptive-controller-in-xbox-accessories-app)

## USER GUIDE

Files available at https://github.com/makersmakingchange/Willow-Joystick | Page 29 of 44

### The Hub Menu

The Hub is an interface device used to connect the Willow joystick and assistive switches to the Host Device. The Hub also contains a display that shows the Hub Menu, an interface for adjusting settings, calibrating the joystick, changing the operating mode, restarting the device, and resetting to the default settings.

Accessing the Hub Menu
The Hub Menu is normally off to reduce power consumption and wear on the screen. To use the Hub Menu, it must first be activated using assistive switches, or the Hub Buttons. The following table shows the corresponding input options to enter/exit the Hub Menu.
Action | Input
On Hub Button | Assistive Switch
Enter/Exit menu | Select very long press (>3 seconds) | S1 very long press (>3 seconds)
Enter/Exit Menu | Simultaneous Press of Next and Sel | Simultaneous Press of S1 and S3

Navigating the Hub Menu
Once the Hub Menu is activated, it will display a list of menus. The current selection will be indicated by a left arrow (>). The Hub Menu is navigated using inputs from assistive switches, and/or the Hub Buttons. The following table shows the corresponding input options to navigate the Hub Menu.
Action | Input
On Hub Button | Assistive Switch
“Next” – goes to next option | Next | S3
“Select” – Selects the pointed to option | Sel | S1

When “Next” is activated, the selection will change to the next item on the list. If “Next” is activated when the selection is on the last item of the list, the selection will change to the top item on the list. A “Next” action is trigged using a short press on S3, or by pressing the Next button on the Hub.

When “Select” is activated, the current selection will be activated, such as opening a submenu, starting calibration, etc. The “Select” action is trigged using a short press on S1, or by pressing the Select button on the Hub.

Hub Menu Options
The Hub Menu is arranged as sets of submenus and pages. Each submenu has a “… Back” option at the end of its list to return to the top of the previous menu. Any selection made will walk you through the required steps with instructions on the Hub Display. The overall structure of the Hub Menu is as follows:

> Exit Menu
> Center Reset
> Mode

## USER GUIDE

Files available at https://github.com/makersmakingchange/Willow-Joystick | Page 30 of 44

> Mouse USB
> Mouse BT
> Gamepad
> Cursor speed
> More
> Sound
> Light Brightness
> Scroll Speed
> Full Calibration
> Restart Willow
> Factory Reset

Exit Menu
The top menu item is to exit and deactivate the Hub Menu. After performing any other setting changes, or backing out of submenus, the menu display will always return to the top of the main menu, so it is easy to exit the menu after changing settings. When selected, you will be asked to confirm you wish to leave the menu and can select “Confirm” to exit, or “… Back” to return to the menu.

As shown in the table for navigating the menus, any function used to enter the menu, can also be used to exit it.

Center Reset
A center reset will reset the neutral resting position of your joystick and should be used if you are experiencing drift. Do not touch the joystick while performing a center reset.

Mode
The Mode submenu allows you to select one of three modes: USB
Mouse, BT Mouse, or Gamepad. Note that it is important to ensure you are in the correct mode for the device you want to connect to. After changing modes, the Hub will reset and perform a center reset upon powering on. Do not touch the joystick until you see the Hub display read “Ready for use” and the mode.

Cursor Speed
The Cursor Speed submenu allows you to increase or decrease the mouse cursor speed in increments of 1 from a scale of 1 to 10. While changing the increment, the cursor can still be moved across the screen to test the current speed setting.

More
The More submenu contains further submenus for settings that likely won’t be used as often.

Sound On/Off
This menu item will toggle the sound feedback for Willow inputs on or off. There is no volume control.

## USER GUIDE

Files available at https://github.com/makersmakingchange/Willow-Joystick | Page 31 of 44

Light Brightness
Thie menu allows you to increase or decrease the brightness of the lights on the Hub in increments of 1 from a scale of 0 to 10.

Scroll Speed
This menu allows you to increase or decrease the mouse scroll speed in increments of 1 from a scale of 1 to 10.

Full calibration
A full calibration is used to set the extents of your joystick and should be done if you are having issues moving in certain directions with the joystick.

Restart Willow
This option provides a way for the user to reset the Willow without physically disconnecting it from power.

Factory Reset
This option will trigger a factor reset that returns all settings back to default. This includes the operating mode, cursor speed, calibrations, and any settings adjusted through the API.

Adjusting the Willow
Adjustments to the Willow involve calibrating the joystick and changing settings. To adjust the Willow, most settings can be changed through the Hub Display menu.

Center Reset
A Center Reset resets the neutral position of the joystick in its resting position. If the position of the cursor is moving when the joystick is released and stationary, a Center Reset can help resolve the cursor drift.

A Center Reset should be performed in the following situations:

1. The Willow mounting angle is adjusted.
2. The Willow topper is replaced.
3. The cursor continues to move when the topper is released and is stationary.

A Center Reset is automatically performed when the Willow is first powered on, and at the end of the Full Calibration process. A Center Reset can also be started manually using the Hub Menu or outside of the menu using a Very Long Press on an Assistive Switch attached to S2:

## USER GUIDE

Files available at https://github.com/makersmakingchange/Willow-Joystick | Page 32 of 44

### 1. Using the Hub Menu:

a. Activate the Hub Menu by applying a very long (>3 seconds) press on the Select Button or S1 and then release it.
i. An alternative way to open the Hub Menu is a simultaneous short press of S1 and S3, or Next and Select on the Hub.
b. The Hub Menu will turn on.
c. Use a short press of the Next button or S3 to move through the Menu options until you reach “Calibration.”
d. Use a Short (<1 seconds) press of the Select Button or S1 to select “Calibration.”
e. Use a Short (<1 seconds) press of the Select Button or S1 to select “Center Reset.”
f. Release the joystick and do not touch it until the menu screen returns to the regular menu.

### 2. Using Long Press on Assistive Switch S2:

a. Perform a Very Long Press (>3 seconds) of S2.
b. Release the joystick and do not touch it until the Hub screen states that the center reset is complete.

When the Center Reset is started, the Hub Menu Display will prompt you to not touch the joystick. It is important to release the joystick and leave it to sit in its neutral resting position to perform the center reset.

Full Calibration
The Full Calibration of the Willow should be completed upon initial assembly of the device. It may also need to be repeated if the user is experiencing strange cursor movements or no change in movement at the extents of the joystick.

The calibration procedure is a timed process that requires the joystick to be moved to each corner of the movement range. The Hub menu display will give prompts to follow for moving the joystick.

### 1. Initiate Full Calibration

a. Apply and maintain a very long (>3 seconds) press of the Select Button or S1 and then release it.
i. An alternative way to open the Hub Menu is a simultaneous short press of S1 and S3, or Next and Select on the Hub.
b. The Hub Menu will turn on.
c. Use a short (<1 second) press of the Next button or S3 to move through the Menu options until you reach “Calibration”
d. Use a short (<1 second) press of the Sel Button or S1 to select “Calibration”
e. Use a short (<1 second) press of the Next button or S3 to move through the Menu options until you reach “Full Calibration.”
f. Use a short (<1 second) press of the Sel Button or S1 to select “Full Calibration”
g. Release the joystick and follow the prompts on the Hub Menu Display.

## USER GUIDE

Files available at https://github.com/makersmakingchange/Willow-Joystick | Page 33 of 44

### 2. Follow Full Calibration Prompts

a. The Hub Display will show “Follow on screen prompts”
b. The Hub will beep once, all lights will flash once, and the Display will show “Hold joystick top left”
i. Move the joystick to the top left corner extent and hold it there until the prompt changes, also signified by the Hub beeping once and all lights flashing once.
c. The Hub Display will show “Hold joystick top right”
i. Move the joystick to the top right corner and hold it there until the prompt changes.
d. The Hub Display will show “Hold joystick bottom right”
i. Move the joystick to the bottom right corner and hold it there until the prompt changes also signified by the Hub beeping once and all lights flashing once.
e. The Hub Display will show “Hold joystick bottom left”
i. Move the joystick to the bottom right corner and hold it there until the prompt changes also signified by the Hub beeping once, in a higher pitch, and all lights flashing once.
f. The Hub Display will show “Release, do not move joystick”
i. Release the joystick back to its neutral position and do not touch it.

### 3. Calibration Complete

a. When the calibration is complete, the Hub Display will show “Joystick Calibrated” and then return to the main menu screen.
b. You can test the joystick movement on the host device screen to ensure the calibration was successful.
c. You can now continue through the menu settings or exit the menu and use your joystick.

## USER GUIDE

Files available at https://github.com/makersmakingchange/Willow-Joystick | Page 34 of 44

Changing Willow Settings
There are numerous settings that control the operation of the Willow. Some of these settings can be adjusted independently through the Hub Menu.

Table 1: Willow Settings
Setting | Default | Min | Max | Note
Cursor Speed | 5 | 0 | 10 | Changes the cursor speed in any Mouse Mode.
Sound Feedback | On | Off | On | Turns the sound on or off.
Light Brightness Level | 5 | 0 | 10 | Adjust the brightness of the LED lights. To turn off the lights completely, set to level 0.
Scroll Speed | 5 | 1 | 10 | Changes the scrolling speed in any Mouse Mode.
Inner Deadzone | 0.05 | 0.0 | 0.5 | Changes the distance the joystick must be moved from rest to cause cursor/gamepad movement. Only adjustable through API, not Hub menu.
Outer Deadzone | 0.95 | 0.5 | 1.0 | Changes the distance the joystick must be moved from the outer edge to provide full cursor/gamepad movement. Only adjustable through API, not Hub menu.

Changing the Cursor Speed
To change the cursor speed, the host device settings can be adjusted, or the Willow cursor speed can be adjusted. To change the Willow cursor speed:
1. The Hub Menu can be activated using a very long press on Select Button or S1; or by a simultaneous short press of S1 and S3, or Next and Select on the Hub.
2. Use a short (<1 second) press of the Next button or S3 to move through the Menu options until you reach “Cursor speed”
3. Use a short (<1 second) press of Sel Button or S1 to select “Cursor speed”
4. Use a short (<1 second) press of Next button or S3 to move through the Menu options “increase” and “decrease”
5. Use a short (<1 second) press of Sel Button or S1 to select “increase” or “decrease” as desired.
a. Note: the minimum cursor speed level is 1, and the maximum is 10.
6. Test the cursor speed on the host device by moving the joystick while in the menu.
7. Once happy with the cursor speed, navigate to “…Back” using a short (<1 second) press of Next button or S3.
8. Use a short (<1 second) press of Sel Button or S1 to select “…Back”
9. Use a short (<1 second) press of Sel Button or S1 to select “Exit Menu” or continue through the menu to adjust other settings.

Changing the Scroll Speed
The scroll speed controls how much the screen scrolls with vertical motion of the joystick when Scroll Mode is activated. To change the WIllow scroll speed:

## USER GUIDE

Files available at https://github.com/makersmakingchange/Willow-Joystick | Page 35 of 44
1. The Hub Menu can be activated using a very long press on Select Button or S1; or by a simultaneous short press of S1 and S3, or Next and Select on the Hub.
2. Use a short (<1 second) press of Next button or S3 to move through the Menu options until you reach “More”
3. Use a short (<1 second) press of Sel Button or S1 to select “More”
4. Use a short (<1 second) press of Next button or S3 to move through the Menu options until you reach “Scroll speed”
5. Use a short (<1 second) press of Sel Button or S1 to select “Scroll speed”
6. Use a short (<1 second) press of Next button or S3 to move through the Menu options “increase” and “decrease”
7. Use a short (<1 second) press of Sel Button or S1 to select “increase” or “decrease” as desired.
a. Note: the minimum scroll speed level is 1, and the maximum is 10.
8. Test the scroll speed on the host device by moving the joystick while in the menu.
9. Once happy with the scroll speed, navigate to “…Back” using a short (<1 second) press of Next button or S3.
10. Use a short (<1 second) press of Sel Button or S1 to select “…Back”
11. Use a short (<1 second) press of Sel Button or S1 to select “Exit Menu” or continue through the menu to adjust other settings.

Changing the Light Brightness
The brightness of the Hub lights can be adjusted to suit the user’s preference. A user may wish to increase the brightness when working in a bright environment or decrease the brightness when working in a dark room. The brightness of the lights can be adjusted from Level 0 (completely off) to Level 10 (full brightness). To change the brightness:
1. The Hub Menu can be activated using a very long press on Select Button or S1; or by a simultaneous short press of S1 and S3, or Next and Select on the Hub.
2. Use a short (<1 second) press of Next button or S3 to move through the Menu options until you reach “More”
3. Use a short (<1 second) press of Sel Button or S1 to select “More”
4. Use a short (<1 second) press of Next button or S3 to move through the Menu options until you reach “Light Brightness”
5. Use a short (<1 second) press of Sel Button or S1 to select “Light Brightness”
6. Use a short (<1 second) press of Next button or S3 to move through the Menu options “increase” and “decrease”
7. Use a short (<1 second) press of Sel Button or S1 to select “Increase” or “Decrease” as desired.
a. Note: the minimum brightness level is 0, and the maximum is 10.
8. The Hubs lights will briefly illuminate to preview the new brightness.

## USER GUIDE

Files available at https://github.com/makersmakingchange/Willow-Joystick | Page 36 of 44
9. Once happy with the brightness, navigate to “…Back” using a short (<1 second) press of Next button or S3.
10. Use a short (<1 second) press of Sel Button or S1 to select “…Back”
11. Use a short (<1 second) press of Sel Button or S1 to select “Exit Menu” or continue through the menu to adjust other settings.

Changing the Sound Mode
Sound feedback can be turned on or off. To change the Willow Sound Mode:
1. The Hub Menu can be activated using a very long press on Select Button or S1; or by a simultaneous short press of S1 and S3, or Next and Select on the Hub.
2. Use a short (<1 second) press of Next button or S3 to move through the Menu options until you reach “More”
3. Use a short (<1 second) press of Sel Button or S1 to select “More”
4. Use a short (<1 second) press of Next button or S3 to move through the Menu options until you reach “Sound”
5. Use a short (<1 second) press of Sel Button or S1 to select “Sound”
6. The current sound mode will be indicated (either ON or OFF).
7. Use a short (<1 second) press of Sel Button or S1 to select “Turn off “ or “Turn on” to toggle the Sound Mode.
8. Once happy with the Sound Mode, navigate to “…Back” using a short (<1 second) press of Next button or S3.
9. Use a short (<1 second) press of Sel Button or S1 to select “…Back”
10. Use a short (<1 second) press of Sel Button or S1 to select “Exit Menu” or continue through the menu to adjust other settings.

Input-Output Mapping
The mapping of inputs (e.g., Short Press, Very Long Press) to actions (e.g., Right Click, Activate Menu) are currently fixed in code and not adjustable by the user. Contact your maker or support for assistance.

Changing Settings Through the Serial Interface (API)
All the user-adjustable settings of the Willow are accessible through the Serial Interface. This is a more challenging method intended only for advanced users. Refer to Appendix A: Serial Interface (Application Programming Interface) for more information.

### Storage

When not in use, the Willow should be stored in a cool place out of direct sunlight.

### Care

The Willow is made of 3D printed plastic. Exposure to high heat may cause warping and/or negatively affect function. Extended exposure to sunlight will also weaken the plastic on the device.

## USER GUIDE

Files available at https://github.com/makersmakingchange/Willow-Joystick | Page 37 of 44

The Willow contains electronics and is not waterproof. If the device becomes wet, make sure it is off and do not use it or power it on until it has completely dried. It may help to open any electronic enclosures to speed up drying and ensure it has completely dried.

Cleaning the Willow
Cleaning the Willow Joystick
✓ | Wipe with a damp cloth
✗ | Don’t use abrasive cleaning materials
✗ | Don’t soak the Willow Joystick in any cleaning
solutions
✗ Don’t immerse the Willow Joystick

Cleaning the Willow Hub
✓ | Wipe plastic enclosure with a damp cloth
✗ | Don’t scrub or press down on the Hub Display
✗ | Don’t use abrasive cleaning materials
✗ | Don’t soak the Willow Hub in any cleaning
solutions
✗ Don’t immerse the Willow Hub in any liquids

## USER GUIDE

Files available at https://github.com/makersmakingchange/Willow-Joystick | Page 38 of 44

## Troubleshooting

Mouse cursor is not visible
- Make sure device is connected
- Make sure device is in the intended operating mode (e.g., USB, not Wireless)
- Make sure the device has proper onscreen settings (e.g., AssistiveTouch on iOS)

Mouse cursor is difficult to see
- Adjust the size or color of the cursor on the host device

Cursor movement is too slow or too fast
- Adjust the cursor speed on the Willow
- Adjust the cursor speed on the host device

Difficulty inputting a double-click
- Adjust host devices double click rate

Cursor / Joystick Drift

- Trigger a center reset
a. Activate the Hub Menu and navigate to Center reset.
b. Using a very long press of Assistive Switch 2
c. Disconnected and reconnect power.

Display reads “No USB. Use menu to change modes”

- If you would like to connect to your device through a Bluetooth connection, simply open the Hub Menu, navigate to Mode, and select “MOUSE BT.” The Willow will reset and there should no longer be any error messages.
- If you are trying to connect to your device through a wired USB connection:
- Check that the host device is powered on and ready to use.
- Check that the Willow is securely plugged in on both ends of the USB cable.
- Make sure you are using a USB-C cable that transmits data, not a power-only cable.
- Try doing a Willow Reset
- If the problem persists, contact support (see below).

Display shows error messages and enters safe mode

1. Disconnect the Hub from power.
2. Wait 15 seconds.
3. Unplug the Willow Interface cable on both ends and plug both ends back in.
4. Reconnect the Hub to power.

If this does not resolve the error, make note of the error code on the Safe Mode menu screen, and refer to Table 2.

## USER GUIDE

Files available at https://github.com/makersmakingchange/Willow-Joystick | Page 39 of 44

### Error Codes

The Willow automatically detects several hardware problems on startup. If an error is detected, a two-tone error sound will play and the device will go in to Safe Mode and display an error code. Table 2 lists the error codes and the corresponding actions to take as a user.

In some cases, a hardware error will be triggered when the power is disconnected and reconnected quickly. This can be resolved by disconnected the USB cable, waiting 30 seconds, and reconnecting the USB. If the problem persists, there might be a problem with the internal sensor or cable.

ERROR-001 can indicate that the Willow Interface cable between the Hub and the Joystick is not connected properly. Disconnect the USB cable from the Hub, check both ends of the Willow Interface Cable are securely attached, then reconnect the USB Cable to the Hub.

Table 2. Willow Error Codes – User
Error Code | Connection Error | User Action Display | Joystick Sensor
ERROR-001 | | ● | 1. Check that the Willow interface cable is securely connected on both ends. 2. Confirm the Willow Interface Cable is the right type. 3. Contact support
ERROR-002 | ● | | 1. Disconnect USB, wait 30 second, reconnect USB. 2. Contact support.
ERROR-003 | ● ●

## USER GUIDE

Files available at https://github.com/makersmakingchange/Willow-Joystick | Page 40 of 44

## Contacting Support

1. Contact the person who made the device.
2. Email info@makersmakingchange.com

## Disposal

PLA filament may be industrially compostable in your area. Check with your waste management company if PLA can be composted or must be thrown in the garbage.

Disassemble the Willow and separate out the recyclable and compostable components, and those that must be thrown out. Electronics and batteries should be disposed of following your local waste management guidelines.

## Appendix A: Serial Interface (Application Programming Interface)

The Willow has an Application Programming Interface that can be used to change settings through a serial interface.

### Serial Interface Setup

To use the API, you will need a host device capable of supporting a serial connection and a serial terminal emulator program. The Arduino IDE¹
is a convenient option.

Serial Settings
Select the appropriate COM port and set the speed to 115200.

### Sending Commands

Once the serial connection is established, text commands can be sent to the Willow. Make sure the line ending is set to ‘No Line Ending’. The commands should be sent in all capitals. Commands are sent in a two step process.

First, send the following command to activate the interface:

SETTINGS

If the serial connection is setup properly, the Willow will respond with:

SUCCESS,0:SETTINGS

Next, send the desired command. The command consists of a two letter end-point code followed by a comma and either a zero or a one. Then, a colon is used to separate the parameter. All of the end-points are listed in Error! Reference source not found..

1 Available at no cost: https://www.arduino.cc/en/software

## USER GUIDE


Files available at https://github.com/makersmakingchange/Willow-Joystick | Page 41 of 44

### API Format Willow Command List

Command | Success Response | Description
SETTINGS | SUCCESS,0:SETTINGS | Enter Settings mode
EXIT | SUCCESS,0:EXIT | Exit Settings mode

Willow Commands

Table 3: Serial Interface Commands

Command | Success Response | Description
MN,0:0 | SUCCESS,0:MN,0:1 | Get Model number
VN,0:0 | SUCCESS,0:VN,0:V{N.NN} | Get version number (V{N.NN})
ID,0:0 | SUCCESS,0:ID,0:{Unique Device ID} | Get Unique Device ID (8 alphanumeric
OM,0:0 | SUCCESS,0:OM | Get operating mode (1 = USB Mouse, 2= USB Gamepad)
OM,1:{OM} | SUCCESS,1:OM | Set operating mode (1 = USB Mouse, 2= USB Gamepad)
CM,0:0 | SUCCESS, 0:CM | Get communication mode value ( 0=No HID Output, 1=USB mode enabled 2=Bluetooth mode enabled )
CM,1:1 | SUCCESS,0:CM,1:1 | Set communication mode value to 1 (USB mode enabled)
CM,1:2 | SUCCESS,0:CM,1:2 | Set communication mode value to 2 (Bluetooth mode enabled)
CM,1:{CM} | | Set Communication Mode (
LM,0:0 | SUCCESS,0:LM | Get light mode (0 = All LEDS off, 1 = Minimal LEDs, 2 = Normal LEDs)
LM,1:{LM} | SUCCESS,1:LM | Set light mode (0 = All LEDS off, 1 = Minimal LEDs, 2 = Normal LEDs)
LL,0:0 | SUCCESS,1:{Light Brightness Level} | Get current light brightness level (0 = Light off, 10 = brightest)
LL,1:{LL} | SUCCESS,1:{Light Brightness Level} | Set light brightness level (0 = Light off, 10 = brightest)
SM,0:0 | SUCCESS,0:SM | Get sound mode (0 = Sound off, 1 = Basic Sound, 2 = All sounds
SM,1:{SM} | SUCCESS,1:SM | Set sound mode (0 = Sound off, 1 = Basic Sound, 2 = All sounds
SS,0:0 | SUCCESS,0:SS,0:{Cursor Speed Level} | Get the mouse cursor speed value (Level)
SS,1:{Cursor Speed Level:0-10} | SUCCESS,0:SS,1:{Cursor Speed Level} | Set the mouse cursor speed value (Level)
SL,0:0 | SUCCESS,0:SL,0:{Scroll Level} | Get the mouse scroll level value. (1-10)

## USER GUIDE

Files available at https://github.com/makersmakingchange/Willow-Joystick | Page 42 of 44
Command | Success Response | Description
SL,1:{Scroll Level:1-10} | SUCCESS,0:SL,1:{Scroll Level} | Set the mouse scroll level value. (1-10)
JV,0:0 | SUCCESS,0,JV,0:{Joystick Value
IN,0:0 | SUCCESS,0:IN,0:{ x|y } | Get current joystick center values (x and y)
IN,1:1 | SUCCESS,0:IN,1:{ x|y } | Activate joystick center reset to set new joystick neutral values (x and y)
CA,0:0 | SUCCESS,0:CA,0:{ x0|y0, x1|y1, x2|y2, x3|y3, x4|y4 } | Get current joystick calibration values (point 0, point 1, point 2, point 3, point 4)
CA,1:1 | SUCCESS,0:CA,1:{ x0|y0 } | Activate full joystick calibration process
| SUCCESS,0:CA,1:{ x1|y1 } | Perform joystick calibration using command (Step 1)
| SUCCESS,0:CA,1:{ x2|y2 } | Perform joystick calibration using command (Step 2)
| SUCCESS,0:CA,1:{ x3|y3 } | Perform joystick calibration using command (Step 3)
| SUCCESS,0:CA,1:{ x4|y4 } | Perform joystick calibration using command (Step 4)
IZ,0:0 | SUCCESS,0:IZ,0:{ Inner Deadzone Factor 0.0 to 1.0 } | Get joystick inner deadzone (0.0 to 1.0)
IZ,1:{ Joystick Inner Deadzone Factor 0.0 to 1.0} | SUCCESS,0:IZ,1:{ Deadzone Factor 0.0 to 1.0 } | Set joystick inner deadzone (0.0 to 1.0)
OZ,0:0 | SUCCESS,0:OZ,0:{ Outer Deadzone Factor 0.0 to 1.0 } | Get joystick outer deadzone (0.0 to 1.0)
OZ,1:{ Joystick Outer Deadzone Factor 0.0 to 1.0} | SUCCESS,0:OZ,1:{ Outer Deadzone Factor 0.0 to 1.0 } | Set joystick outer deadzone (0.0 to 1.0)
CH,1,{Menu Control} | SUCCESS,1,CH,1:{Menu Control} | Control Hub Menu ( 0=No action, 1=Open Menu, 2=Select Item, 3=Next Item, 4=Close Menu)
DM,0:0 | SUCCESS,0:DM,0:{Debug Mode} | Get debug mode value ( 0=debug mode off, 1=joystick debug mode 3=button debug mode 4=switch debug mode)
DM,1:0 | SUCCESS,0:DM,1:0 | Set debug mode value to 0 (Disabled)
DM,1:1 | SUCCESS,0:DM,1:1 | Set debug mode value to 1 (joystick debug mode enabled)
DM,1:3 | SUCCESS,0:DM,1:3 | Set debug mode value to 3 (button debug mode enabled)
DM,1:4 | SUCCESS,0:DM,1:4 | Set debug mode value to 4 (switch debug mode enabled)
RT,1:{Test Number} | SUCCESS,1:RT,1:{Test Number} | Run Test ( 1=LED Test, 2=Sound Test, 3=Watchdog Test)
SR,1:1 | SUCCESS,0:RS,1:1 | Perform a soft reset.
FR,1:1 | SUCCESS,0:FR,1:1 | Perform factory reset

## USER GUIDE

Files available at https://github.com/makersmakingchange/Willow-Joystick | Page 43 of 44

Response Code
Response
Status

Response
Code

Description

SUCCESS | 0 | The command has successfully performed.
FAIL | 0 | The serial API mode is not enabled. Please enter the serial API mode.
FAIL | 1 | The requested command does not exist. Returns the response code and the requested parameter.
FAIL | 2 | The requested command exists, but the entered parameter is in incorrect format. Returns the response code and the requested parameter.
FAIL | 3 | The requested command exists, but the entered parameter is out of range. Returns the response code and the current value stored in the Flash.

Debug Mode
Debug
Mode
Debug Mode | OUTPUT
0 | Debug Mode Off | None
1 | Joystick Debug Mode | DEBUG,1:{ raw x | raw y [mT], filtered x | filtered y [, output x | output y}
3 | Button Debug Mode | DEBUG,3:{ Main State, Secondary State, Elapsed Time}
4 | Switch Debug Mode | DEBUG,4:{ Main State, Secondary State, Elapsed Time}

Table 4. Button Debug Mode

States | Buttons
Main State | Button1 + 2*Button2 + 4*Button3 | 0 = No buttons pushed, 1 = Next button pushed, 2 = Select button pushed, 3 = Both buttons pushed
Secondary State | Waiting = 0, Started = 1, Released = 2
Elapsed Time | Time in ms since start of current state

## USER GUIDE

Files available at https://github.com/makersmakingchange/Willow-Joystick | Page 44 of 44
States | Button Debug Mode | Switch Debug Mode
Main State | Button1 + 2*Button2: 0 = No buttons pushed, 1 = Next button pushed, 2 = Select button pushed, 3 = Both buttons pushed | Switch1 + 2* Switch2 + 4* Switch3: 0 = No Switches pressed; 1 =
Secondary State | Waiting = 0, Started = 1, Released = 2 | Waiting = 0, Started = 1, Released = 2
Elapsed Time | Time in ms since start of current state | Time in ms since start of current state

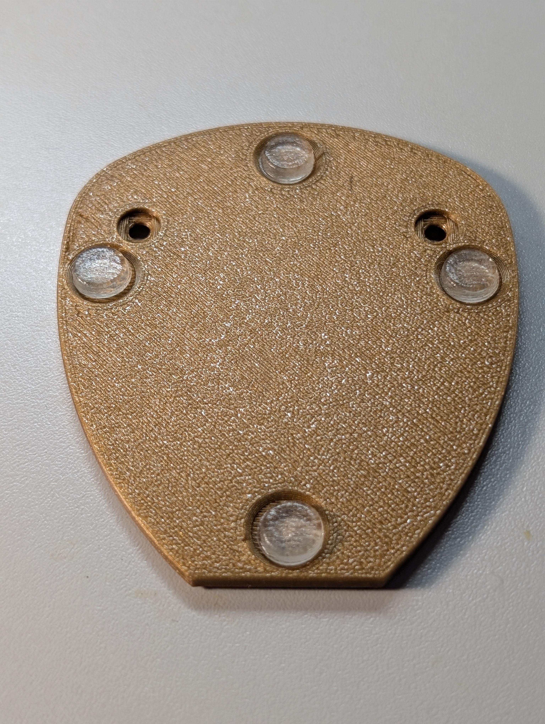
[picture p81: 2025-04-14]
Documentation/Working_Documents/Assets/Assembled non slip base.jpg

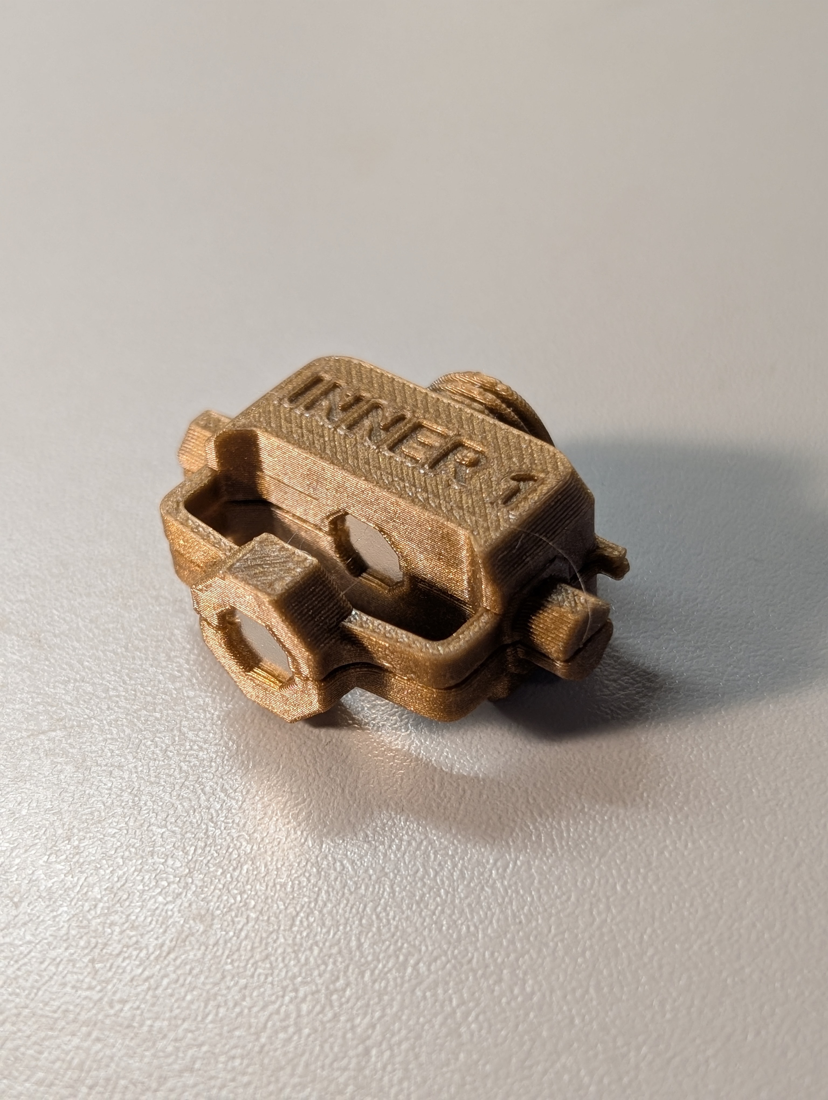
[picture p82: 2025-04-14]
Documentation/Working_Documents/Assets/Step 2.jpg

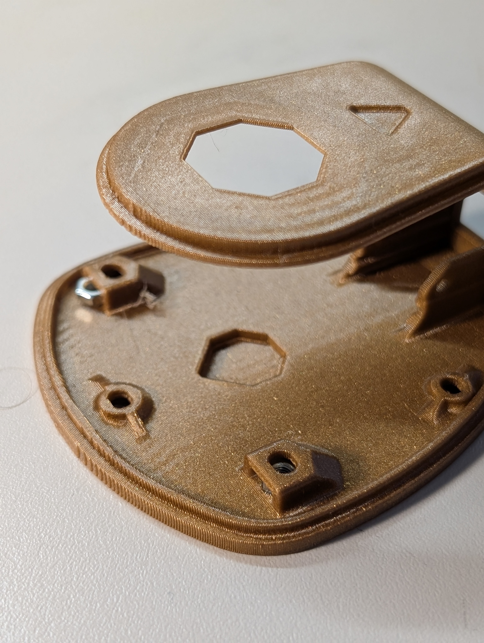
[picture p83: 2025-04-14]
Documentation/Working_Documents/Assets/Step 14 1.jpg

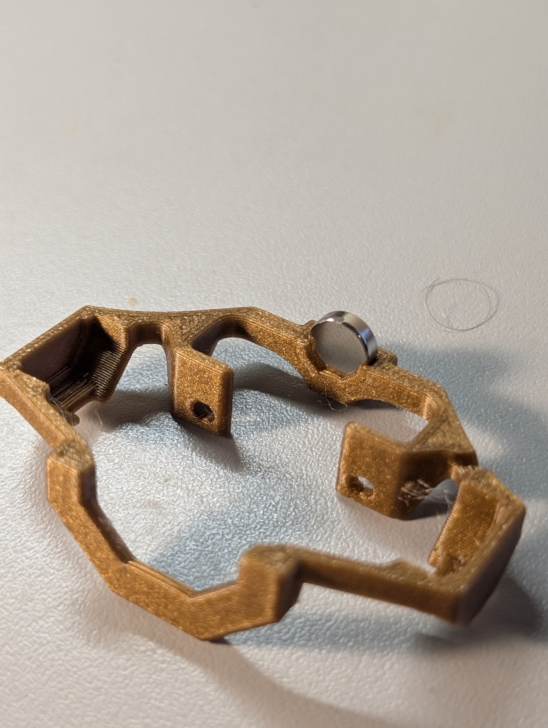
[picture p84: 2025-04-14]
Documentation/Working_Documents/Assets/Step 12.jpg

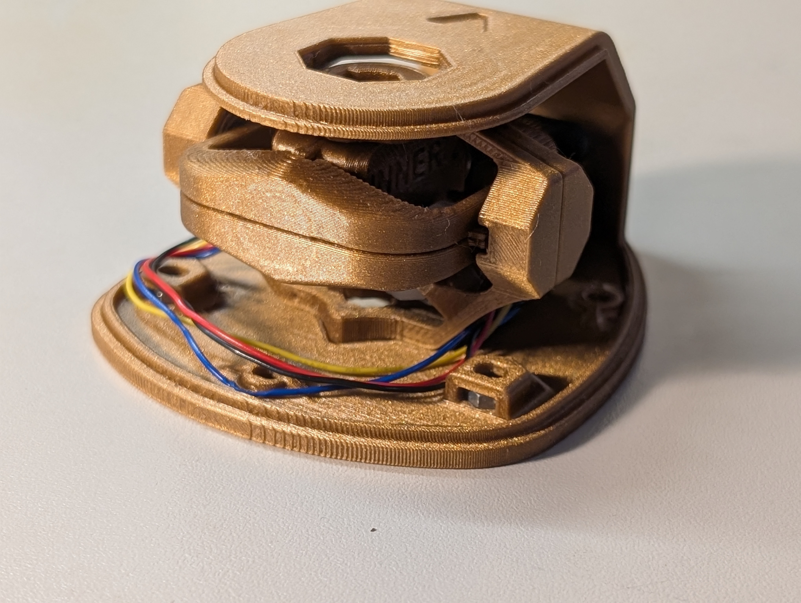
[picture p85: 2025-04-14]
Documentation/Working_Documents/Assets/Step 16 3.jpg

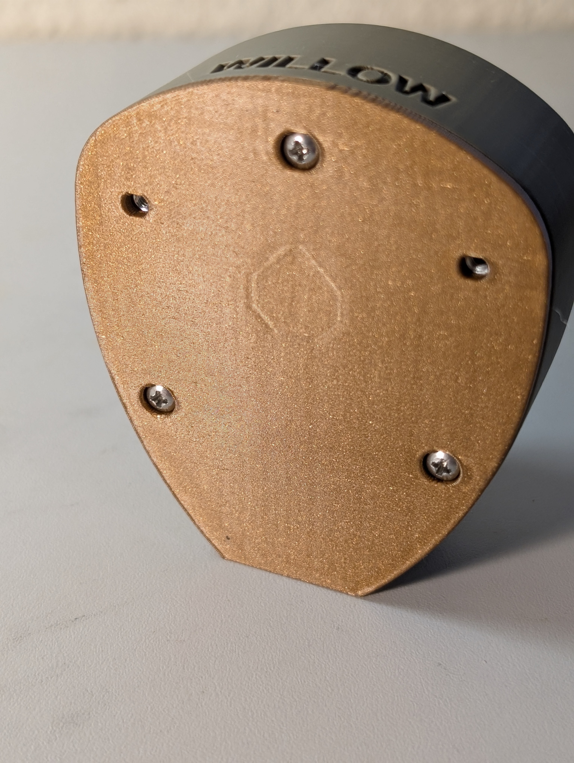
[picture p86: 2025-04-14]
Documentation/Working_Documents/Assets/Step 17 2.jpg

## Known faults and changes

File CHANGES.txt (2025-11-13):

Version 1.0.1 | 2025-11-13
 - Added direct download link to the Arduino library for the magnetic sensor board
 - Updated Maker Guide to include how to import the downloaded zip library

Version 1.0.0 | 2025-04-09
 - Updated CAD to final release
 - Added non slip base
 - Added more wrist ramps
 - Updated toppers to gutter lock
 - New firmware based on LipSync 4.1 release
 - Added full documentation
 - Added design files

Version 0.9.0 | 2025-02-13
 - Initial Prototype
 - Magnetic low-force joystick
 - Range of swappable, customizable toppers
 - Available mounting adapters
 - Available wrist ramp
 - Available nonslip base
 - Uses existing LipSync Hub

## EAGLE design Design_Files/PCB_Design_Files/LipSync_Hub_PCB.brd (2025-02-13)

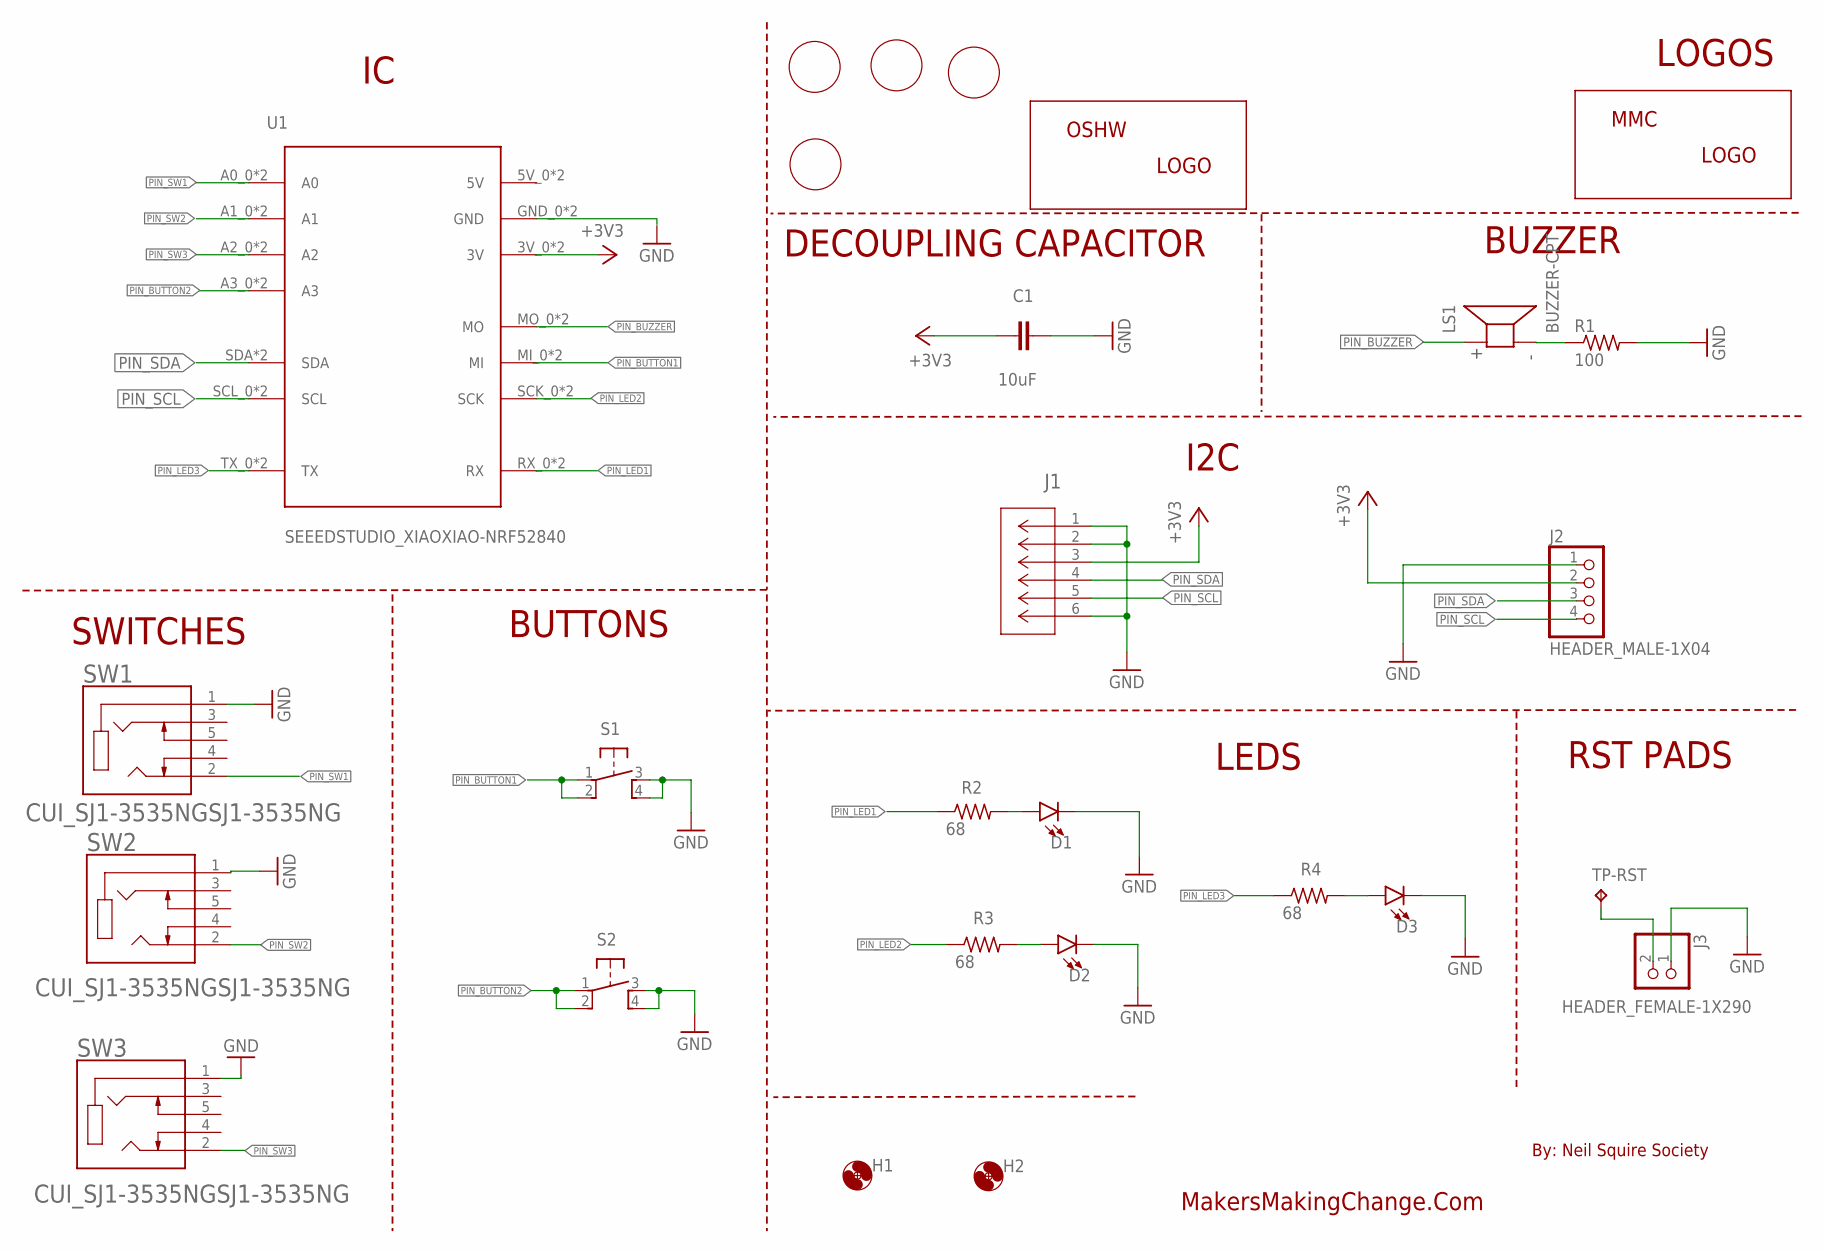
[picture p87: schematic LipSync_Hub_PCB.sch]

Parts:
C1: 10uF; CAP-050-030X075
D1, D2, D3: LED_5MM-5MM-RED-LONG; LED_5MM_RED_LONG
H1, H2: MOUNT-HOLE-3MM-CLEAR; HOLE-3MM-CLEAR
J1: 5555165-1; CONN6_5555165-1
J2: HEADER_MALE-1X04
J3: HEADER_FEMALE-1X290; HEADER_FEMALE-1X02_90
LOGO-BACK: MMC_LABEL-BACK; LABEL-BACK
LOGO-FRONT: MMC_LABEL-FRONT; LABEL-FRONT
LOGO-LIPSYNC-BACK: MMC_LABEL-LIPSYNC-X-LG; LABEL-LIPSYNC-X-LG
LOGO-MMC-BACK: MMC_LOGO-MD; MMC_MEDIUM_LOGO
LOGO-NORTH: MMC_LABEL-UP; LABEL-UP
LOGO-OSWH: OSHW_LOGO-SM; OSHW_SMALL_LOGO
LS1: BUZZER-CPT; CUI_CPT-1255C-090
R1: 100; RESISTOR_0205/7
R2, R3, R4: 68; RESISTOR_0205/7
S1, S2: SWITCH_OMRON-PTH-12; B3F-5050
SW1, SW2, SW3: CUI_SJ1-3535NGSJ1-3535NG; CUI_SJ1-3535NG
TP-RST: TESTPAD_TPB1,27; TESTPAD_B1,27
U1: SEEEDSTUDIO_XIAOXIAO-NRF52840; SEEEDSTUDIO_XIAO_NRF52840

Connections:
+3V3: C1.2, J1.3, J2.2, U1.3V_0 (3V), U1.3V_1 (3V)
GND: C1.1, D1.K (C), D2.K (C), D3.K (C), J1.1, J1.2, J1.6, J2.1, J3.1, R1.2, S1.3, S1.4, S2.3, S2.4, SW1.1, SW2.1, SW3.1, U1.GND_0 (GND), U1.GND_1 (GND)
unnamed: LS1.N, R1.1
unnamed: D2.A, R3.2
unnamed: J3.2, TP-RST.TP
unnamed: D3.A, R4.2
unnamed: D1.A, R2.2
PIN_BUTTON1: S1.1, S1.2, U1.MI_0 (MI), U1.MI_1 (MI)
PIN_BUTTON2: S2.1, S2.2, U1.A3_0 (A3), U1.A3_1 (A3)
PIN_BUZZER: LS1.P, U1.MO_0 (MO), U1.MO_1 (MO)
PIN_LED1: R2.1, U1.RX_0 (RX), U1.RX_1 (RX)
PIN_LED2: R3.1, U1.SCK_0 (SCK), U1.SCK_1 (SCK)
PIN_LED3: R4.1, U1.TX_0 (TX), U1.TX_1 (TX)
PIN_SCL: J1.5, J2.4, U1.SCL_0 (SCL), U1.SCL_1 (SCL)
PIN_SDA: J1.4, J2.3, U1.SDA, U1.SDA_0 (SDA)
PIN_SW1: SW1.2, U1.A0_0 (A0), U1.A0_1 (A0)
PIN_SW2: SW2.2, U1.A1_0 (A1), U1.A1_1 (A1)
PIN_SW3: SW3.2, U1.A2_0 (A2), U1.A2_1 (A2)

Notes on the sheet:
By: Neil Squire Society
MakersMakingChange.Com
SWITCHES
BUZZER
I2C
DECOUPLING CAPACITOR
LOGOS
BUTTONS
LEDS
RST PADS

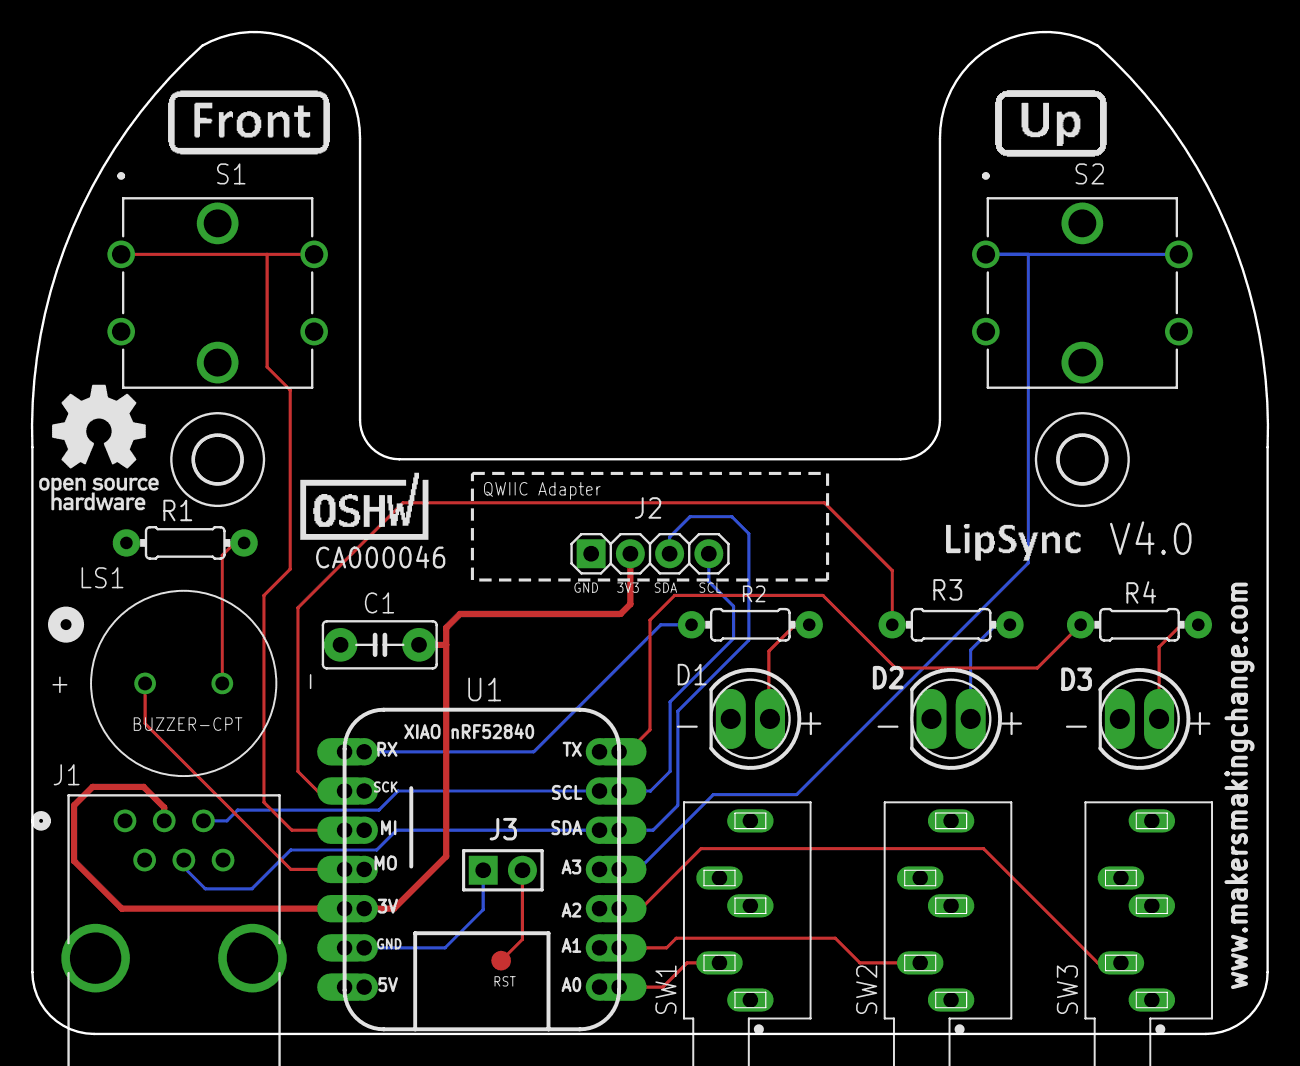
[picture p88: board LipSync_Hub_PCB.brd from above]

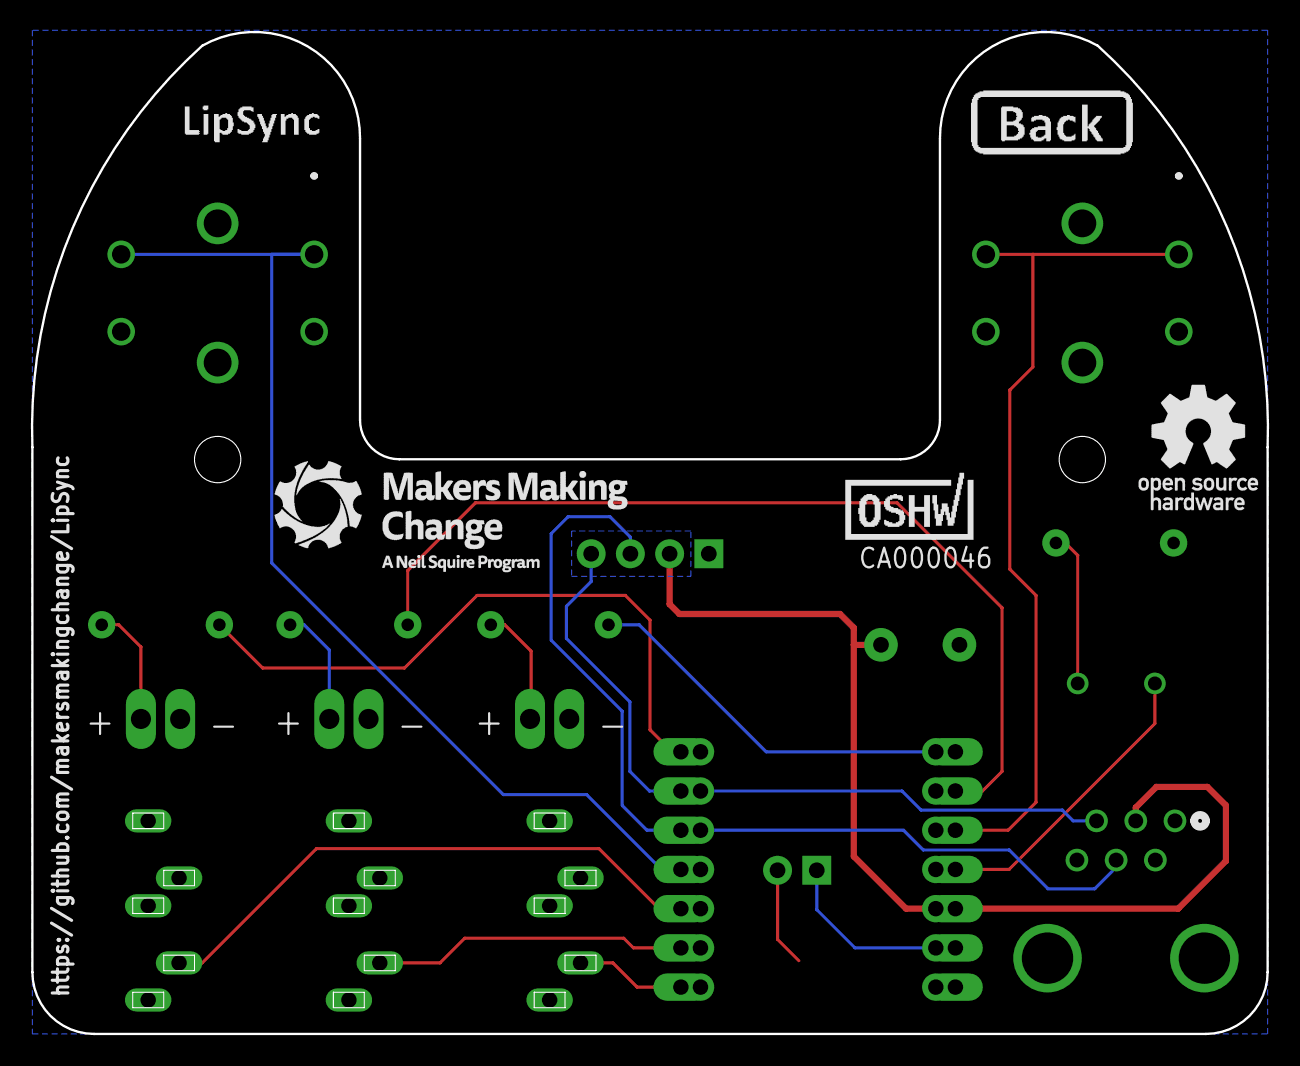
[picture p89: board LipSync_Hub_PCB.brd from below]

Board: 2 copper layers, 80.0 x 64.9 mm, 31 parts (5 on the bottom side), 18 nets.

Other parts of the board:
U$1: OSHW_SMALL_LOGO
U$2, U$4: CA000046; CERT-SMALL-SILK
U$3: LABEL-LIPSYNC-X-LG

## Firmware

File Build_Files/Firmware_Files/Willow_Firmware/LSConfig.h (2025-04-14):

/* 
* File: LSConfig.h
* Firmware: Willow
* Developed by: MakersMakingChange
* Version: v1.0rc (April 4 2025)
  License: GPL v3.0 or later

  Copyright (C) 2024 - 2025 Neil Squire Society
  This program is free software: you can redistribute it and/or modify it under the terms of
  the GNU General Public License as published by the Free Software Foundation,
  either version 3 of the License, or (at your option) any later version.
  This program is distributed in the hope that it will be useful, but WITHOUT ANY WARRANTY;
  without even the implied warranty of MERCHANTABILITY or FITNESS FOR A PARTICULAR PURPOSE.
  See the GNU General Public License for more details.
  You should have received a copy of the GNU General Public License along with this program.
  If not, see <http://www.gnu.org/licenses/>

*/

#include "LSUtils.h"

// Debugging
#define USB_DEBUG  0 // Set this to 0 for best performance
#define SHOW_CONNECTION_TIME 0 // Set to 0 for production

#define CONF_ENABLE_WATCHDOG 1 // Set to 1 to enable hardware watchdog

//***DO NOT CHANGE***//
#define CONF_WILLOW_MODEL 1                // 1: Willow w/ Hub

#define CONF_WILLOW_VERSION_MAJOR  1
#define CONF_WILLOW_VERSION_MINOR  0
#define CONF_WILLOW_VERSION_REV  0

const String willowVersionStr = String(CONF_WILLOW_VERSION_MAJOR) + "." + String(CONF_WILLOW_VERSION_MINOR) + "." + String(CONF_WILLOW_VERSION_REV);

// I2C Devices
#define I2CADDR_DISPLAY 0x3D  // Display address (61)
#define I2CADDR_TLV493D 0x5E  // 3D Hall Effect Sensor (94)


// Input pins
#define CONF_BUTTON1_PIN 9                  // Pushbutton S1
#define CONF_BUTTON2_PIN 3                  // Pushbutton S2
#define CONF_SWITCH1_PIN A0                 // 3.5 mm jack SW1
#define CONF_SWITCH2_PIN A1                 // 3.5 mm jack SW2
#define CONF_SWITCH3_PIN A2                 // 3.5 mm jack SW3

// Input buttons and switch values 
#define CONF_BUTTON_NUMBER 2
#define CONF_SWITCH_NUMBER 3

// Output LEDS
#define CONF_LED_LEFT_PIN 7                 // left
#define CONF_LED_MIDDLE_PIN 8               // middle
#define CONF_LED_RIGHT_PIN 6                // right

// Onboard LEDs
#define CONF_LED_MICRO_RED LED_RED          // Xiao NRF52840 User LED Red
#define CONF_LED_MICRO_GREEN LED_GREEN      // Xiao NRF52840 User LED Green
#define CONF_LED_MICRO_BLUE LED_BLUE        // Xiao NRF52840 User LED Blue

// Output Buzzer
#define CONF_BUZZER_PIN 10

// Operating Mode Values
#define CONF_OPERATING_MODE_MIN 0
#define CONF_OPERATING_MODE_NONE 0
#define CONF_OPERATING_MODE_MOUSE 1
#define CONF_OPERATING_MODE_GAMEPAD 2
#define CONF_OPERATING_MODE_SAFE 3
#define CONF_OPERATING_MODE_MAX 3

#define CONF_OPERATING_MODE_DEFAULT CONF_OPERATING_MODE_MOUSE  // Default mode = Mouse
                                          // 0 = Operating Mode null
                                          // 1 = Mouse
                                          // 2 = Gamepad  

// Communication mode values 
#define CONF_COM_MODE_MIN  0
#define CONF_COM_MODE_NONE 0 
#define CONF_COM_MODE_USB  1
#define CONF_COM_MODE_BLE  2
#define CONF_COM_MODE_MAX  2

#define CONF_COM_MODE_DEFAULT CONF_COM_MODE_USB

#define CONF_LED_NONE 0
#define CONF_LED_LEFT 1
#define CONF_LED_MIDDLE 2
#define CONF_LED_RIGHT 3
#define CONF_LED_MICRO 4
#define CONF_LED_ALL 5

#define CONF_LED_BRIGHTNESS 150

// LED color codes
#define LED_CLR_NONE 0
#define LED_CLR_BLUE 1
#define LED_CLR_PURPLE 2
#define LED_CLR_MAGENTA 3
#define LED_CLR_PINK 4
#define LED_CLR_RED 5
#define LED_CLR_ORANGE 6
#define LED_CLR_YELLOW 7
#define LED_CLR_GREEN 8
#define LED_CLR_TEAL 9
#define LED_CLR_WHITE 10

#define LED_ACTION_NONE 0
#define LED_ACTION_OFF 1
#define LED_ACTION_ON 2
#define LED_ACTION_BLINK 3
#define LED_ACTION_BLINKFAST 4

// Display
#define CONF_DISPLAY_ENABLED false

// Button Input States
#define INPUT_MAIN_STATE_NONE           0
#define INPUT_MAIN_STATE_S1_PRESSED     1
#define INPUT_MAIN_STATE_S2_PRESSED     2
#define INPUT_MAIN_STATE_S12_PRESSED    3
#define INPUT_MAIN_STATE_S3_PRESSED     4
#define INPUT_MAIN_STATE_S13_PRESSED    5
#define INPUT_MAIN_STATE_S23_PRESSED    6
#define INPUT_MAIN_STATE_S123_PRESSED   7


// Output action numbers
#define CONF_ACTION_NOTHING 0              // No action
#define CONF_ACTION_LEFT_CLICK 1           // Generates a short left click
#define CONF_ACTION_RIGHT_CLICK 2          // Generates a short right click
#define CONF_ACTION_MIDDLE_CLICK 3         // Generates a short middle click
#define CONF_ACTION_DRAG 4                 // Initiates drag mode, holding down left click until cancelled
#define CONF_ACTION_SCROLL 5               // Initiates scroll mode. Vertical motion generates mouse scroll wheel movement.
#define CONF_ACTION_B1_PRESS 6             // Generates a Button 1 press or button X1(Left USB)/View(Right USB) press in XAC  
#define CONF_ACTION_B2_PRESS 7             // Generates a Button 2 press or button X2(Left USB)/Menu(Right USB) press in XAC    
#define CONF_ACTION_B3_PRESS 8             // Generates a Button 3 press or button LS(Left USB)/RS(Right USB) press in XAC
#define CONF_ACTION_B4_PRESS 9             // Generates a Button 4 press or button LB(Left USB)/RB(Right USB) press in XAC 
#define CONF_ACTION_B5_PRESS 10            // Generates a Button 5 press or button A(Left USB)/X(Right USB) press in XAC
#define CONF_ACTION_B6_PRESS 11            // Generates a Button 6 press or button B(Left USB)/Y(Right USB) press in XAC
#define CONF_ACTION_B7_PRESS 12            // Generates a Button 7 press or button View(Left USB)/X1(Right USB) press in XAC  
#define CONF_ACTION_B8_PRESS 13            // Generates a Button 8 press or button Menu(Left USB)/X2(Right USB) press in XAC 
#define CONF_ACTION_CURSOR_CENTER 14       // Center the joystick 
#define CONF_ACTION_CURSOR_CALIBRATION 15  // Initiates the joystick calibration.
#define CONF_ACTION_DEC_SPEED 16           // Decrease cursor movement speed
#define CONF_ACTION_INC_SPEED 17           // Increase cursor movement speed
#define CONF_ACTION_CHANGE_MODE 18         // Change communication mode
#define CONF_ACTION_START_MENU 19          // Start menu on display
#define CONF_ACTION_STOP_MENU 20           // Close menu on display
#define CONF_ACTION_NEXT_MENU_ITEM 21      // Move to next item in menu
#define CONF_ACTION_SELECT_MENU_ITEM 22    // Select current item in menu 
#define CONF_ACTION_RESET 23               // Software Reset
#define CONF_ACTION_FACTORY_RESET 24       // Factory Reset


// Flash Memory settings - Don't change  
#define CONF_SETTINGS_FILE    "/settings.txt"
#define CONF_SETTINGS_JSON    "{\"MN\":0,\"VN1\":4,\"VN2\":1,\"VN3\":0,\"ID\":0,\"OM\":1,\"CM\":1,\"SS\":5,\"SL\":5,\"PM\":2,\"ST\":3.0,\"PT\":3.0,\"AV\":0,\"IZ\":0.05,\"OZ\":0.95,\"CA0\":[0.0,0.0],\"CA1\":[-13.0,13.0],\"CA2\":[13.0,13.0],\"CA3\":[13.0,-13.0],\"CA4\":[-13.0,-13.0],\"SM\":1,\"LM\":1,\"LL\":5,\"DM\":0}"

// Polling rates for each module
#define CONF_JOYSTICK_POLL_RATE 20          // 20 ms 
#define CONF_SCROLL_POLL_RATE 30            // 30 ms
#define CONF_INPUT_POLL_RATE 20             // 20 ms
#define CONF_BT_FEEDBACK_POLL_RATE 1000     // 1s         
#define CONF_DEBUG_POLL_RATE 100            // 100 ms
#define CONF_SCREEN_POLL_RATE 20            // 20 ms
#define CONF_USB_POLL_RATE 1000             // Check USB connection every 1 second
#define CONF_WATCHDOG_POLL_RATE 5000        // Reset watchdog timer every 5 seconds

#define CONF_BUTTON_PRESS_DELAY 150         // 150 ms - Duration of single button press in gamepad mode

#define CONF_WATCHDOG_TIMEOUT_SEC 30        // 30 second hardware watchdog


// Safe Boot Mode
#define CONF_SAFE_MODE_REASON_WATCHDOG 1
#define CONF_SAFE_MODE_REASON_INPUT 2
#define CONF_SAFE_MODE_REASON_HARDWARE 3

// Hub Menu
#define CONF_SPLASH_SCREEN_DURATION 10000   // 10 seconds - how long the splash screen stays on on startup
#define CONF_SAFEMODE_MENU_TIMEOUT 3000 // 3 seconds between screens
#define CONF_MENU_TIMEOUT  300000           // 300 seconds (5 minutes) - duration of inactivity after which the screen turns off 
#define CONF_MENU_CONTROL_MIN 0
#define CONF_MENU_CONTROL_OPEN 1
#define CONF_MENU_CONTROL_SELECT 2
#define CONF_MENU_CONTROL_NEXT 3
#define CONF_MENU_CONTROL_CLOSE 4
#define CONF_MENU_CONTROL_MAX 4


#define CONF_USB_HID_TIMEOUT  5000           // 5 seconds - timeout for connecting to USB and continuing with the program
#define CONF_USB_HID_INIT_DELAY 2000         // initial delay before attempting to reconnect to usb again

// Polling Timer IDs for each module
#define CONF_TIMER_JOYSTICK 0
#define CONF_TIMER_INPUT 1
#define CONF_TIMER_BLUETOOTH 2
#define CONF_TIMER_DEBUG 3
#define CONF_TIMER_SCROLL 4
#define CONF_TIMER_SCREEN 5
#define CONF_TIMER_USB 6
#define CONF_TIMER_WATCHDOG 7

#define CONF_TIMER_LED_STARTUP 0
#define CONF_TIMER_LED_IBM 1
#define CONF_TIMER_LED_BLINK 2
#define CONF_TIMER_LED_BT 3
#define CONF_TIMER_LED_ERROR 4


// Joystick values 
#define CONF_JOY_CURSOR_SPEED_LEVEL_MIN 1
#define CONF_JOY_CURSOR_SPEED_LEVEL_MAX 10



// Debug mode values 
#define CONF_DEBUG_MODE_NONE      0 
#define CONF_DEBUG_MODE_JOYSTICK  1
#define CONF_DEBUG_MODE_BUTTON    3
#define CONF_DEBUG_MODE_SWITCH    4

#define CONF_DEBUG_MODE_MIN 0
#define CONF_DEBUG_MODE_MAX 5

// Debug Default settings
#define CONF_DEBUG_MODE_DEFAULT  0        // Default debug mode state = Off 
                                          // 0 = Debug mode is Off
                                          // 1 = Joystick debug mode is On
                                          // 2 = Pressure debug mode is On
                                          // 3 = Buttons debug mode is On
                                          // 4 = Switch debug mode is On
                                          // 5 = Sip & Puff state debug mode is On


// Internal Test
#define CONF_TEST_MODE_MIN 1
#define CONF_TEST_MODE_LED 1
#define CONF_TEST_MODE_BUZZER 2
#define CONF_TEST_MODE_WATCHDOG 3
#define CONF_TEST_MODE_MAX 3


// Sound Modes                                                                                              
#define CONF_SOUND_MODE_OFF     0   // Sound off
#define CONF_SOUND_MODE_BASIC   1   // Minimal sounds
#define CONF_SOUND_MODE_ALL     2   // All sounds

#define CONF_SOUND_MODE_MIN     0
#define CONF_SOUND_MODE_MAX     2
#define CONF_SOUND_MODE_DEFAULT CONF_SOUND_MODE_BASIC


// Light Modes
#define CONF_LIGHT_MODE_OFF     0   // LEDs off
#define CONF_LIGHT_MODE_BASIC   1   // Minimal LEDs
#define CONF_LIGHT_MODE_ALL     2   // All LEDs

#define CONF_LIGHT_MODE_MIN     0
#define CONF_LIGHT_MODE_MAX     2
#define CONF_LIGHT_MODE_DEFAULT CONF_LIGHT_MODE_BASIC

// Light Brightness Levels
#define CONF_LED_BRIGHTNESS_LEVEL_DEFAULT   5
#define CONF_LED_BRIGHTNESS_LEVEL_MIN       0
#define CONF_LED_BRIGHTNESS_LEVEL_MAX       10

#define CONF_LED_BRIGHTNESS_MAX 255

//***CAN BE CHANGED***//
// API
#define CONF_API_ENABLED true               // Enable or Disable API

// Startup Default settings
#define CONF_STARTUP_LED_STEP_TIME 500      // Time for each color

// Joystick Deadzone Default settings
#define CONF_JOY_DEADZONE_MIN 0.0
#define CONF_JOY_DEADZONE_INNER_DEFAULT 0.05
#define CONF_JOY_DEADZONE_OUTER_DEFAULT 0.95
#define CONF_JOY_DEADZONE_MAX 1.0
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

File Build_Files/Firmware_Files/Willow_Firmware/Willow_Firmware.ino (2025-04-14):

/* 
* File: Willow_Firmware.ino
* Firmware: Willow
* Developed by: MakersMakingChange
* Version: v1.0rc (April 4 2025)
  License: GPL v3.0 or later

  Copyright (C) 2024 - 2025 Neil Squire Society
  This program is free software: you can redistribute it and/or modify it under the terms of
  the GNU General Public License as published by the Free Software Foundation,
  either version 3 of the License, or (at your option) any later version.
  This program is distributed in the hope that it will be useful, but WITHOUT ANY WARRANTY;
  without even the implied warranty of MERCHANTABILITY or FITNESS FOR A PARTICULAR PURPOSE.
  See the GNU General Public License for more details.
  You should have received a copy of the GNU General Public License along with this program.
  If not, see <http://www.gnu.org/licenses/>
*/

#include <String.h>
#include <Wire.h>
#include "LSUtils.h"
#include "LSConfig.h"
#include "LSTimer.h"
#include <ArduinoJson.h>
#include "LSOutput.h"
#include "LSUSB.h"
#include "LSBLE.h"
#include "LSCircularBuffer.h"
#include "LSInput.h"
#include "LSJoystick.h"
#include "LSMemory.h"
#include "LSScreen.h"
#include "LSBuzzer.h"
#include "LSWatchdog.h"

// Unique ID
String g_deviceUID = "";  // Global variable for storing unique identifier for board

// Communication mode and debug mode variables
int g_comMode;        // 0 = None , 1 = USB , 2 = Wireless
int g_operatingMode;  // 0 = None, 1 = Mouse, 2 = Gamepad, 3 = Safe
int g_soundMode;      // 0 = None, 1 = Basic, 2 = Advanced // TODO 2025-Feb-05 Currently not used - buzzer.begin sets sound mode from memory
int g_lightMode;      // 0 = None, 1 = Basic, 2 = Advanced

int g_debugMode;  // 0 = Debug mode is Off
                  // 1 = Joystick debug mode is On
                  // 3 = Buttons debug mode is On
                  // 4 = Switch debug mode is On

int g_errorCode = 0;  // Global variable for storing error code. 0 is no error. Additional errors defined in LSConfig.h

uint32_t g_lastRebootReason = 0;
bool g_watchdogReset = false;
bool g_safeModeEnabled = false;
int  g_safeModeReason = 0;
bool readyToUseFirstTime = true;

bool g_btIsConnected = false;   // Bluetooth connection state
bool g_usbIsConnected = false;  // USB Connection state

bool g_displayConnected = false;                   // Display connection state
bool g_joystickSensorConnected = false;            // Joystick sensor connection state

// LED module variables
ledStateStruct* ledCurrentState = new ledStateStruct;  // pointer to LED current state structure
bool ledActionEnabled = false;

// Input module variables
int buttonActionSize, switchActionSize;
unsigned long buttonActionMaxTime, switchActionMaxTime;
inputStateStruct buttonState, switchState;

int inputButtonPinArray[] = { CONF_BUTTON1_PIN, CONF_BUTTON2_PIN };
int inputSwitchPinArray[] = { CONF_SWITCH1_PIN, CONF_SWITCH2_PIN, CONF_SWITCH3_PIN };

LSInput ib(inputButtonPinArray, CONF_BUTTON_NUMBER);  // Instance of input button object (tactile buttons on Hub)
LSInput is(inputSwitchPinArray, CONF_SWITCH_NUMBER);  // Create an instance of the input switch object (external switches)


// Timer related variables
int actionTimerId[1];  // 1 action timer
LSTimer<int> actionTimer;

int calibrationTimerId[2];  // 2 calibration timers: 0 - , 1-
LSTimer<int> calibrationTimer;

int pollTimerId[10];  // 9 poll timers
LSTimer<void> pollTimer;

int ledTimerId[5];  // 3 LED timers 0 - startup feedback, 1 - IBM, 2- normal blinks, 3 - Bluetooth Status, 4 - error
LSTimer<ledStateStruct> ledStateTimer;

int usbConnectTimerId[1];
LSTimer<int> usbConnectTimer;

unsigned int g_usbAttempt = 0;
unsigned int g_usbConnectDelay = CONF_USB_HID_INIT_DELAY;
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

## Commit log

2024-09-24 Initial commit
    Initial GitHub Commit
    [OpenAT_Placard.f3d, OpenAT_Placard.stl, Willow_Joystick_BOM.xlsx]
2024-11-27 Updated with MVP testing files
    [Joystick_Camera_Mount_Adapter.stl, Joystick_RAM_B_Mount_Adapter.stl, OpenAT_Placard.stl, Willow_Hub_Bottom.stl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]
2024-11-27 Added new device photo
2025-02-13 Stage 4 Willow files
    Updated willow files to stage 4 level
    [Concave Topper.f3d, Convex Topper.f3d, Goalpost Topper Large.f3d, Goalpost Topper Medium.f3d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]
2025-02-13 Added some design files
    [LipSync_Hub_PCB.brd, LipSync_Hub_PCB.sch]
2025-03-04 Updated photos, build files and design files to V1.0
    [Concave Topper.f3d, Convex Topper.f3d, LipSync_Hub_PCB.brd, LipSync_Hub_PCB.sch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]
2025-03-07 Updated Documentation for V1.0 Release
    [Willow_Joystick_BOM.xlsx]
2025-03-26 Removed pressure and SaP from config
2025-03-26 Removed pressure from API
2025-03-26 Removed pressure from main file
2025-04-04 Removed old firmware, added correct dates/names on current firmware
2025-04-08 Updated documentation
    [Willow_Joystick_BOM.xlsx]
2025-04-09 Move PCB files
    [LipSync_Hub_PCB.brd, LipSync_Hub_PCB.sch]
2025-04-09 Added STEP files to design files
    [Concave Topper.step, Convex Topper.step, Goalpost Topper Medium.step, Goalpost Topper Small.step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]
2025-11-13 Magnetic sensor library update
    Added direct download link to the magnetic sensor library and added instructions on how to import it into Arduino
    [Willow_Joystick_BOM.xlsx]

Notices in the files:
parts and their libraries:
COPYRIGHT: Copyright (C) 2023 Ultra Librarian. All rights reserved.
